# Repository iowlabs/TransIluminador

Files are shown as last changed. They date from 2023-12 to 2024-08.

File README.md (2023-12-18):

# TransIluminador

Un transiluminador es un instrumento utilizado en experimentos de biología molecular principalmente en procesos de electroforesis en aplicaciones de PCR, clonación, secuenciación o detección de ADN. Su principio se basa en transmitir luz de longitud e intensidad específica a travez de una muestra, lo cual permite visualizar proteinas específicas o ADN.

Para efectos de la instrumentación, consiste en un dispositivo que controla una gran cantidad de LEDs. De este modo, el dipositivo debe encargarse de generar los voltajes de operación y la corriente de los LEDs. Las variables objetivo para ser controladas son:

- voltaje de operación.
- Intensidad de iluminación.
- Tiempo de exposición.

En algunos dispositivos más complejos existen variables como tipos de curva de iluminación, o algunos cuentan con cámaras para la obtención de imagenes en el dispositivo mismo.
asdavsd

## Requisitos del dispositivo.

El dispositivo a desarrollar debe contar con las siguientes caracteristicas:

1. Alimentación de entrada de 12V. De esto se desprende que el dispositivo debe contar con un regulador DCDC tipo boost para los LEDs.

2. Capacidad de controlar diferentes configuraciónes de LEDs de salida.

3. Control de intensidad de los LEDs por medio de un control lineal de corriente.

4. Driver de corriente de hasta 1A por canal.

4. Capacidad para controlar de forma simultanea 2 canales.

5. Lazo de control para monitoreo y calibración de intensidad luminica.

6. Microcontrolador integrado.

7. Modo de operación manual, stand-alone con curvas pre-configuradas o modo de conexión a un host( pc o web app).

8. Monitoreo de la temperatura de los LEDs y sensor de temperatura externo.

9. Interfaz de usuario por medio de panel y pantalla OLED.

## Revisión del componentes.

Led driver de corriente ajustable

Modulo: LD06AJSA

Amazon: https://www.amazon.com/Adjustable-Current-Driver-30-1500mA-Constant/dp/B07S9C5QF1
Aliexpress: https://es.aliexpress.com/item/32848783838.html?gatewayAdapt=glo2esp

Datasheet no disponible, por observación es un potenciometro y una resistencia de 2.2k aparentemente
Parecido a ejemplos del datasheet de CN5711

Utiliza un CN5711

Datasheet: https://html.alldatasheet.com/html-pdf/1133252/CONSONANCE/CN5711/1403/2/CN5711.html

Otra opción pero más estrecho es NSI50150ADT4G controla entre 150 - 350 mA, 50V Vak max

Datasheet: https://www.onsemi.com/pdf/datasheet/nsi50150ad-d.pdf

Otra opción en rango similar al anterior es MAX16815 35mA - 100 mA
o MAX 16828 35mA - 200 mA
Voltaje de entrada entre 6.5 - 40 V

Datasheet: https://www.analog.com/media/en/technical-documentation/data-sheets/MAX16815-MAX16828.pdf

Existe la posibilidad de hacer una fuente de corriente con 2 PNP y 2 resistencias, la corriente resultante sera producto de ambas resistencias, se puede utilizar una entrada logica o directa para el funcionamiento, se puede reemplazar una ressitencia con un potenciometro y conseguir una fuente variable
Revisar archivo Modulo de corriente.asc

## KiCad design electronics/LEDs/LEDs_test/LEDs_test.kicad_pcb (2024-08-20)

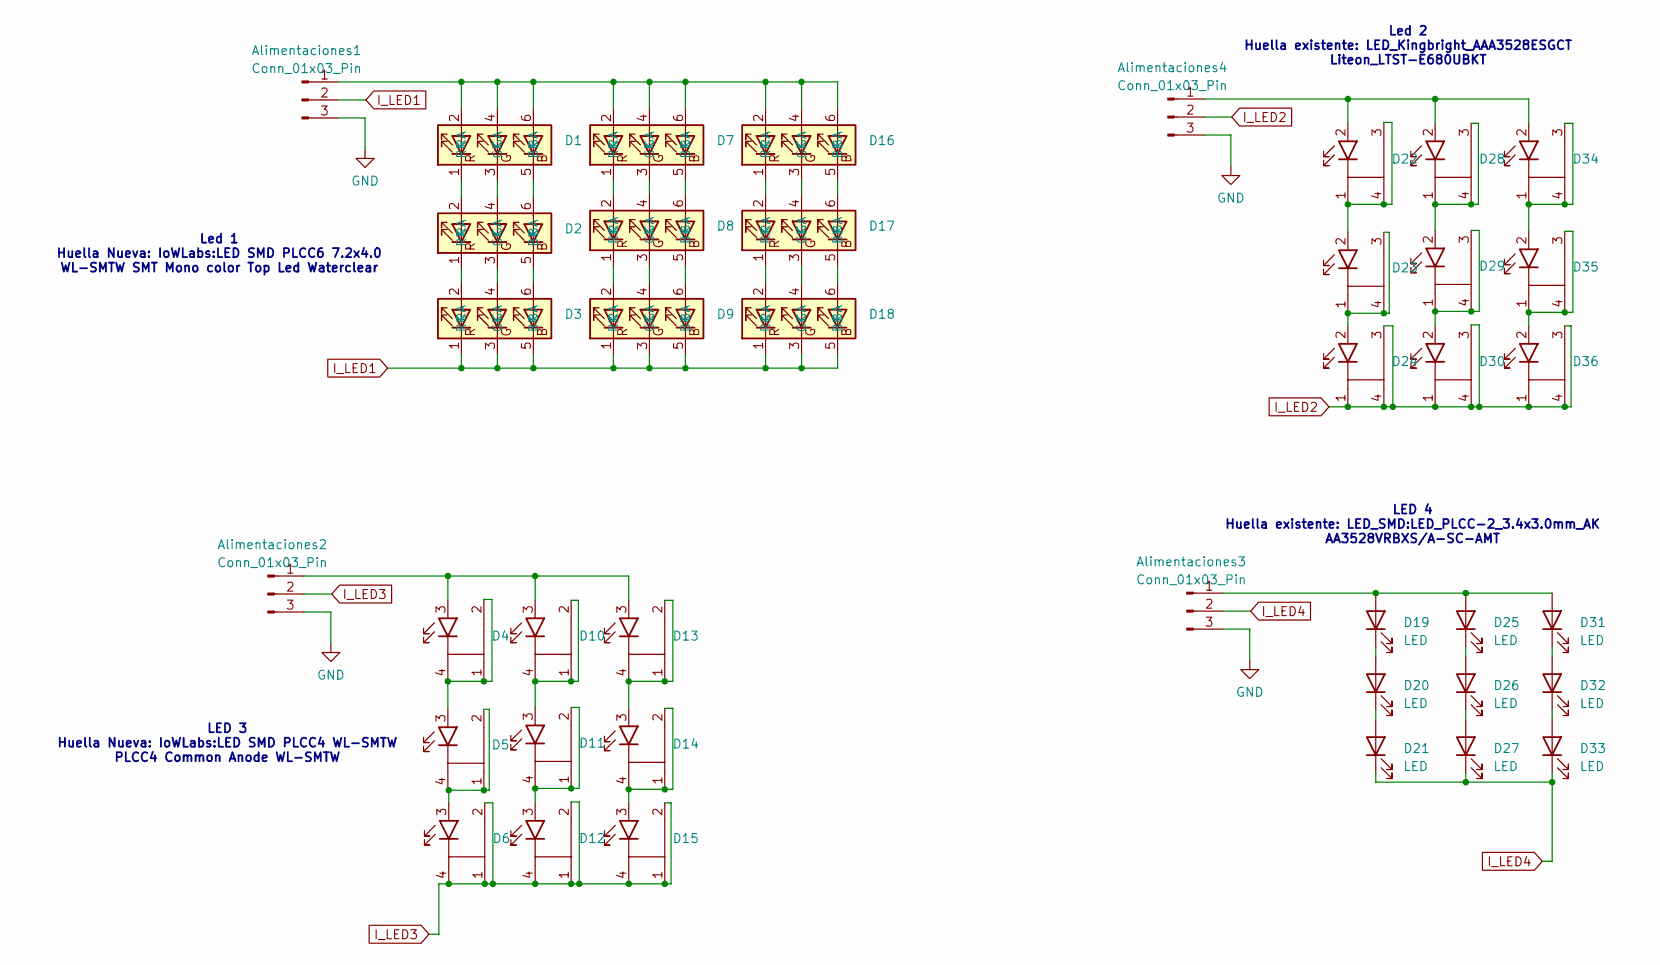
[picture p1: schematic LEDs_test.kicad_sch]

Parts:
Alimentaciones1, Alimentaciones2, Alimentaciones3, Alimentaciones4: Conn_01x03_Pin; JST_XH_B3B-XH-A_1x03_P2.50mm_Vertical
D1, D2, D3, D7, D8, D9, D16, D17, D18: LED SMD PLCC6 7.2x4.0
D4, D5, D6, D10, D11, D12, D13, D14, D15: LED SMD PLCC4 WL-SMTW
D19, D20, D21, D25, D26, D27, D31, D32, D33: LED; LED_PLCC-2_3.4x3.0mm_AK
D22, D23, D24, D28, D29, D30, D34, D35, D36: LED_Kingbright_AAA3528ESGCT

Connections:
GND: Alimentaciones1.3, Alimentaciones2.3, Alimentaciones3.3, Alimentaciones4.3
I_LED1: Alimentaciones1.2, D3.1 (RK), D3.3 (GK), D3.5 (BK), D9.1 (RK), D9.3 (GK), D9.5 (BK), D18.1 (RK), D18.3 (GK), D18.5 (BK)
I_LED2: Alimentaciones4.2, D24.1, D24.3, D24.4, D30.1, D30.3, D30.4, D36.1, D36.3, D36.4
I_LED3: Alimentaciones2.2, D6.1, D6.2, D6.4, D12.1, D12.2, D12.4, D15.1, D15.2, D15.4
I_LED4: Alimentaciones3.2, D21.1 (K), D27.1 (K), D33.1 (K)
unnamed: Alimentaciones1.1, D1.2 (RA), D1.4 (GA), D1.6 (BA), D7.2 (RA), D7.4 (GA), D7.6 (BA), D16.2 (RA), D16.4 (GA), D16.6 (BA)
unnamed: Alimentaciones2.1, D4.3, D10.3, D13.3
unnamed: Alimentaciones3.1, D19.2 (A), D25.2 (A), D31.2 (A)
unnamed: Alimentaciones4.1, D22.2, D28.2, D34.2
unnamed: D1.5 (BK), D2.6 (BA)
unnamed: D1.3 (GK), D2.4 (GA)
unnamed: D1.1 (RK), D2.2 (RA)
unnamed: D2.5 (BK), D3.6 (BA)
unnamed: D2.3 (GK), D3.4 (GA)
unnamed: D2.1 (RK), D3.2 (RA)
unnamed: D4.1, D4.2, D4.4, D5.3
unnamed: D5.1, D5.2, D5.4, D6.3
unnamed: D7.5 (BK), D8.6 (BA)
unnamed: D7.3 (GK), D8.4 (GA)
unnamed: D7.1 (RK), D8.2 (RA)
unnamed: D8.5 (BK), D9.6 (BA)
unnamed: D8.3 (GK), D9.4 (GA)
unnamed: D8.1 (RK), D9.2 (RA)
unnamed: D10.1, D10.2, D10.4, D11.3
unnamed: D11.1, D11.2, D11.4, D12.3
unnamed: D13.1, D13.2, D13.4, D14.3
unnamed: D14.1, D14.2, D14.4, D15.3
unnamed: D16.5 (BK), D17.6 (BA)
unnamed: D16.3 (GK), D17.4 (GA)
unnamed: D16.1 (RK), D17.2 (RA)
unnamed: D17.5 (BK), D18.6 (BA)
unnamed: D17.3 (GK), D18.4 (GA)
unnamed: D17.1 (RK), D18.2 (RA)
unnamed: D19.1 (K), D20.2 (A)
unnamed: D20.1 (K), D21.2 (A)
unnamed: D22.1, D22.3, D22.4, D23.2
unnamed: D23.1, D23.3, D23.4, D24.2
unnamed: D25.1 (K), D26.2 (A)
unnamed: D26.1 (K), D27.2 (A)
unnamed: D28.1, D28.3, D28.4, D29.2
unnamed: D29.1, D29.3, D29.4, D30.2
unnamed: D31.1 (K), D32.2 (A)
unnamed: D32.1 (K), D33.2 (A)
unnamed: D34.1, D34.3, D34.4, D35.2
unnamed: D35.1, D35.3, D35.4, D36.2

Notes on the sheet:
LED 4 Huella existente: LED_SMD:LED_PLCC-2_3.4x3.0mm_AK AA3528VRBXS/A-SC-AMT
Led 1 Huella Nueva: IoWLabs:LED SMD PLCC6 7.2x4.0 WL-SMTW SMT Mono color Top Led Waterclear
Led 2 Huella existente: LED_Kingbright_AAA3528ESGCT Liteon_LTST-E680UBKT
LED 3 Huella Nueva: IoWLabs:LED SMD PLCC4 WL-SMTW PLCC4 Common Anode WL-SMTW

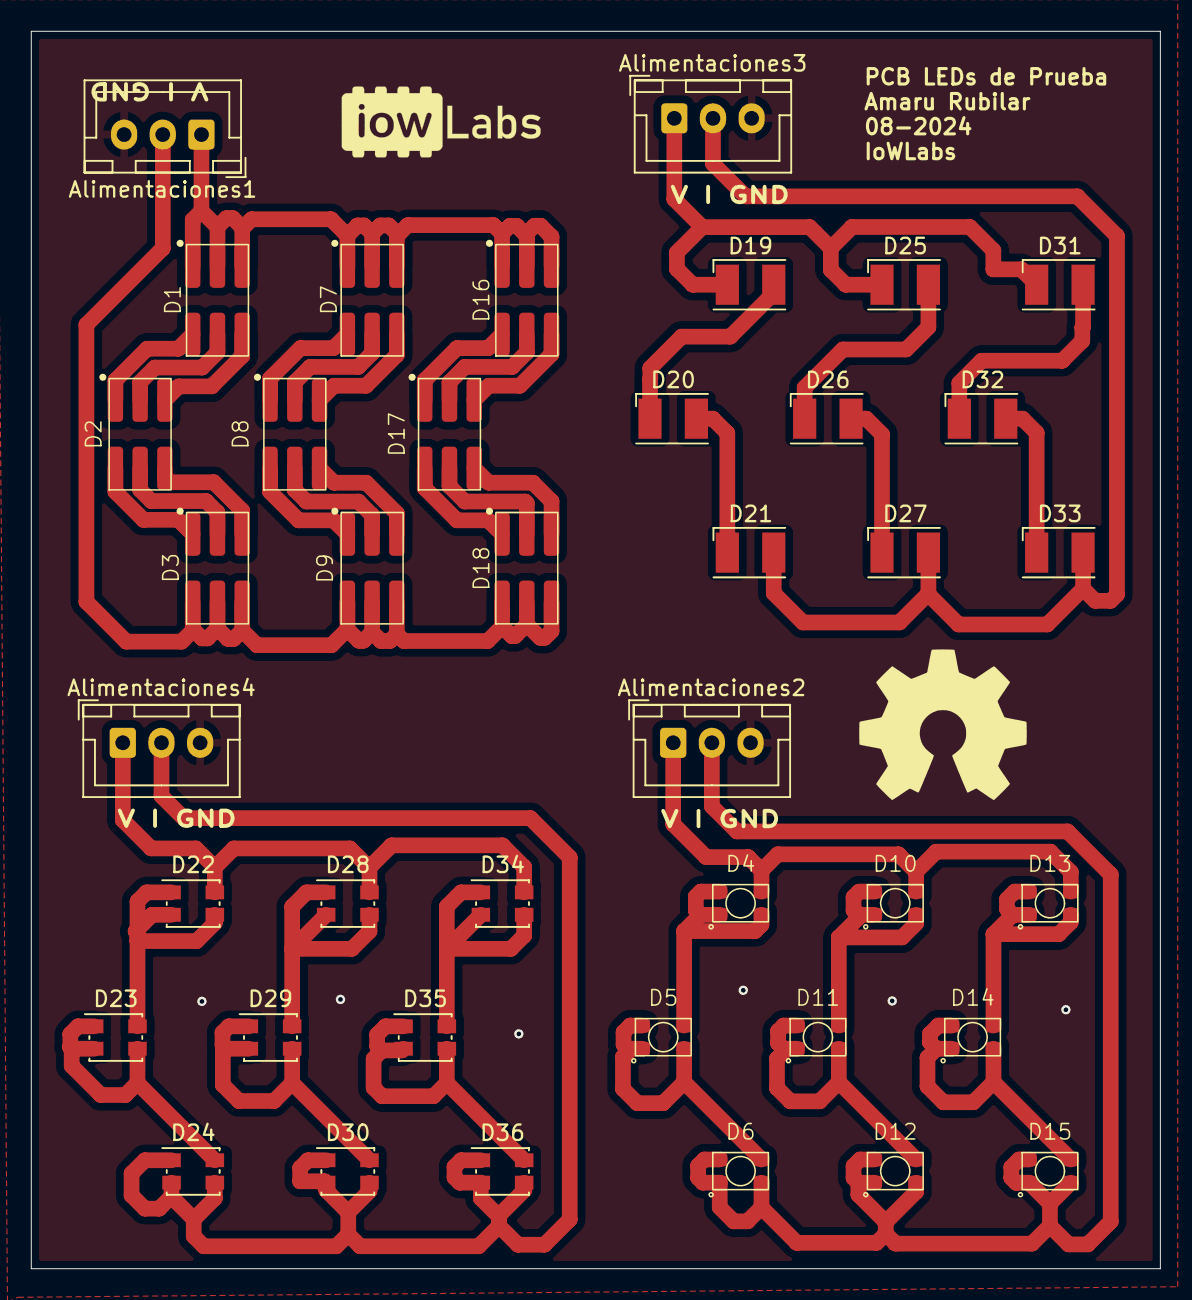
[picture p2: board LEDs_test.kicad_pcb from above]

Board: 2 copper layers, 73.0 x 80.0 mm, 40 parts (0 on the bottom side), 45 nets.

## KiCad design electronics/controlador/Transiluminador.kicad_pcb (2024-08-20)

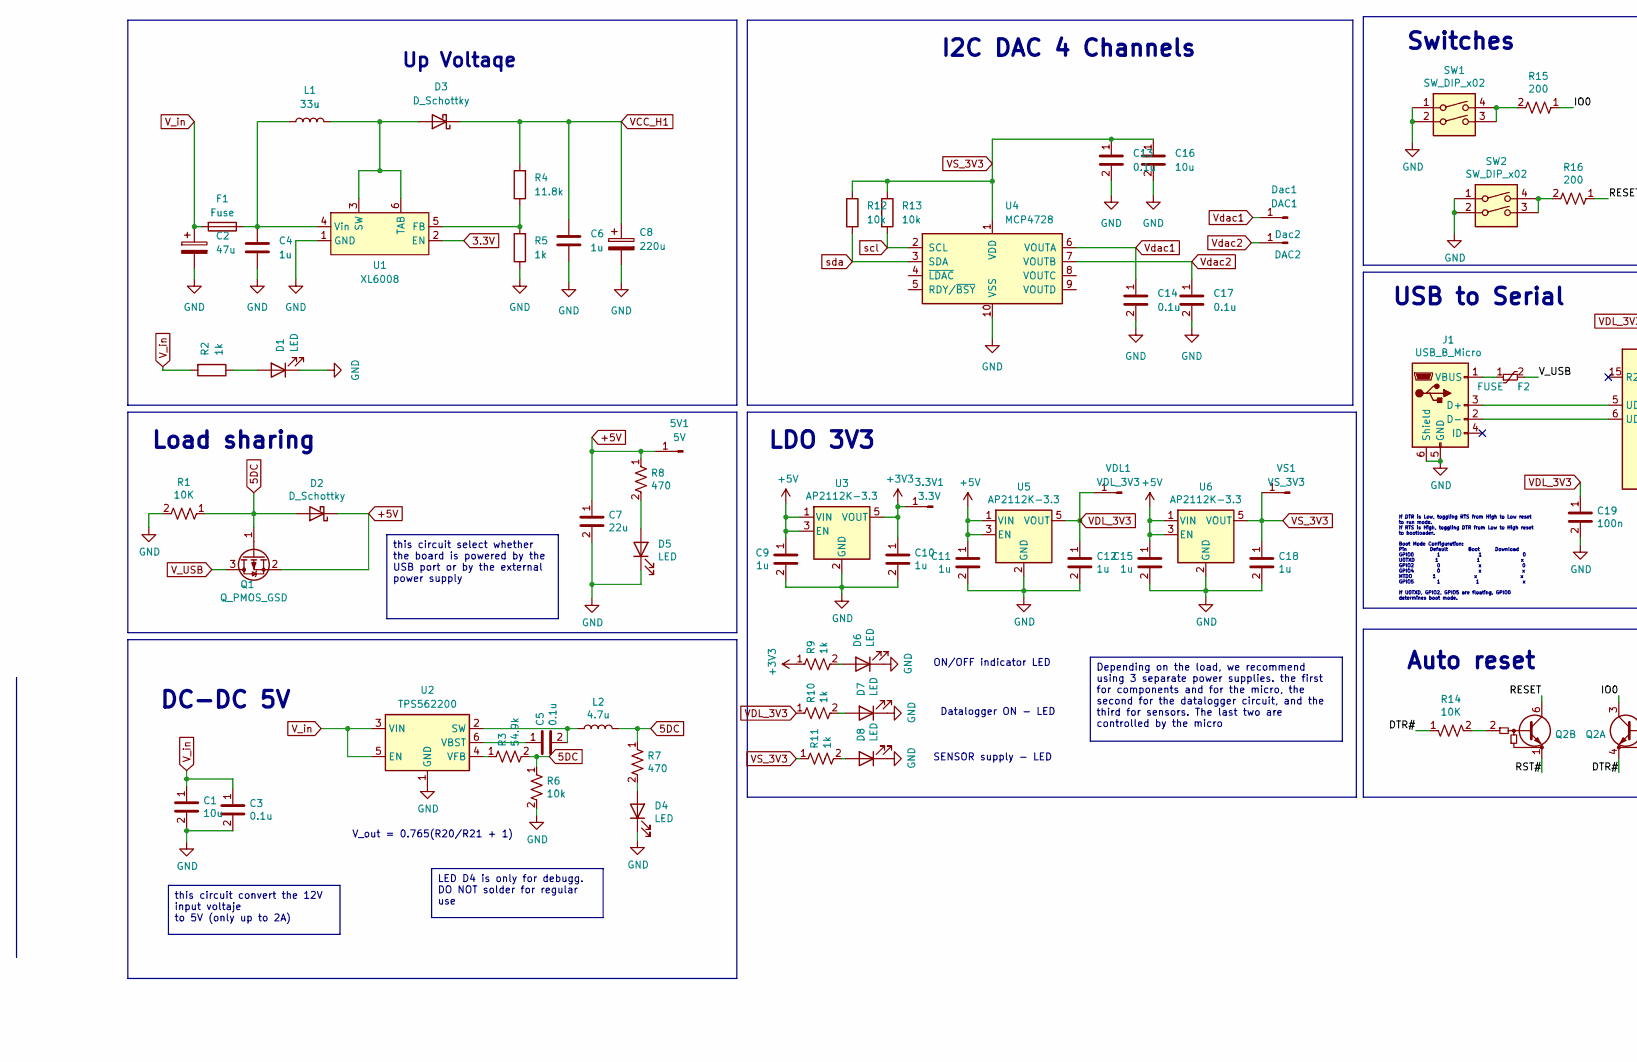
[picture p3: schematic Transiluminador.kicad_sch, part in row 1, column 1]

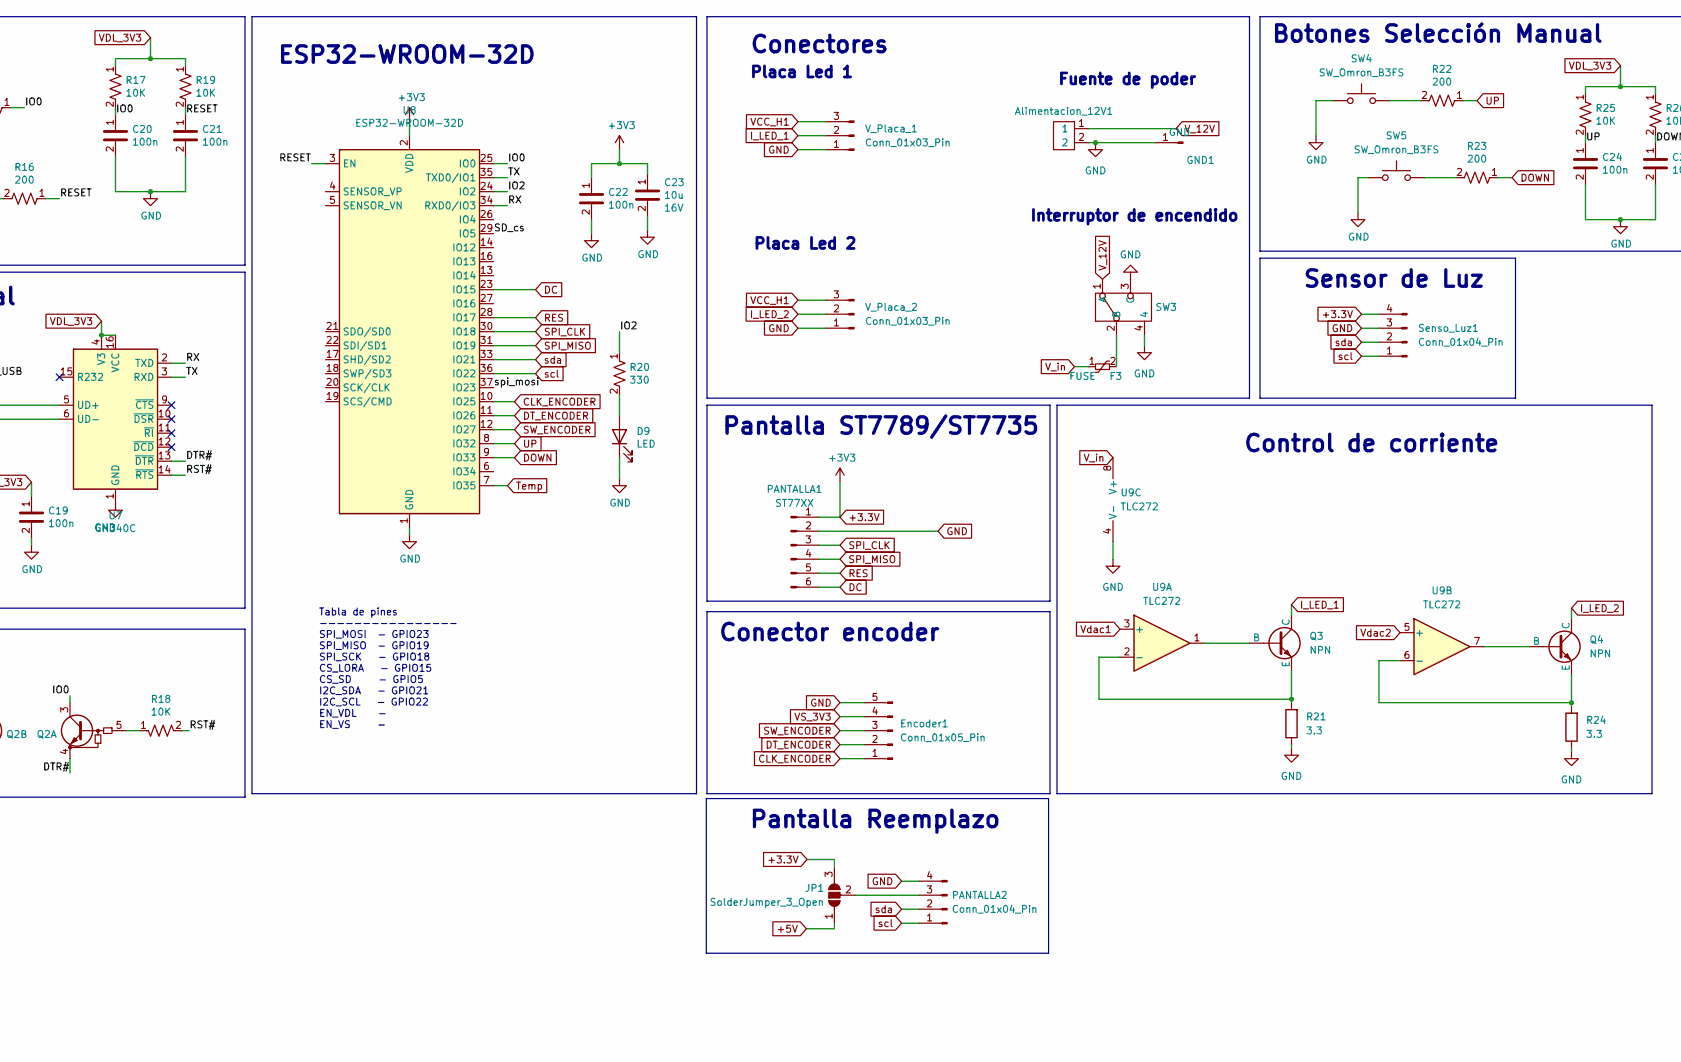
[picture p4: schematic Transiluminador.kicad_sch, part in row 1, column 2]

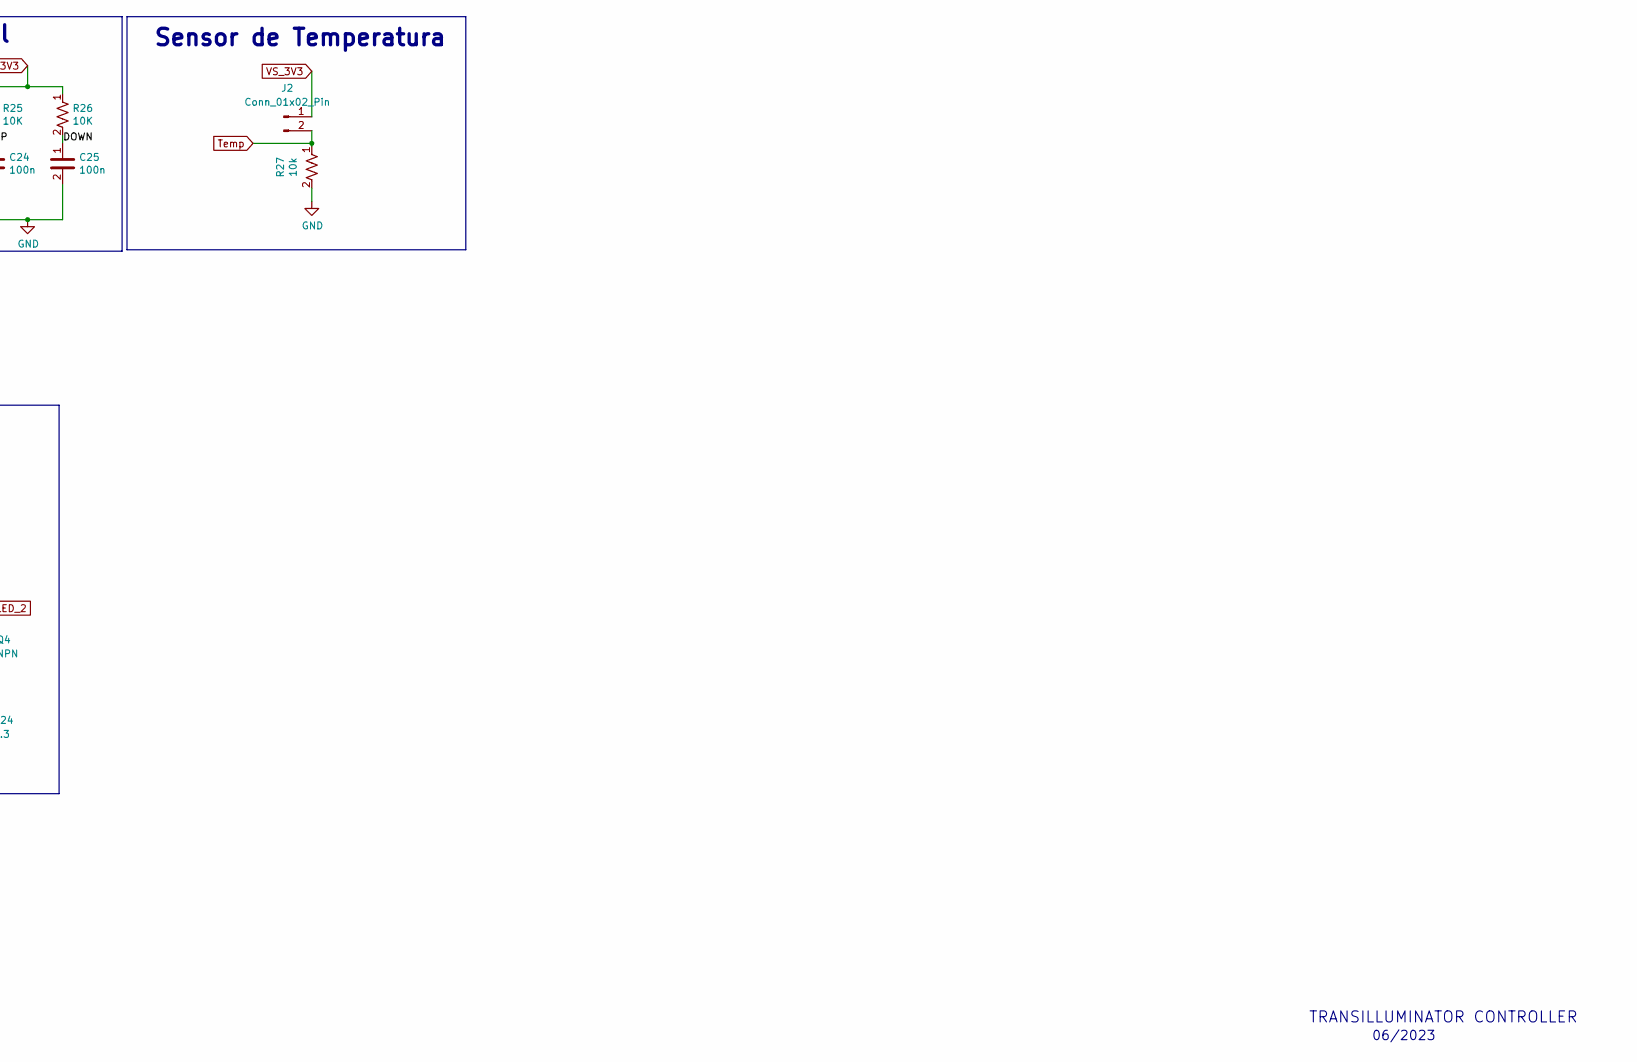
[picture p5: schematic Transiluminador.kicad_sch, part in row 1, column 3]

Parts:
3.3V1: 3.3V; TestPoint_Loop_D2.50mm_Drill1.0mm_LowProfile
5V1: 5V; TestPoint_Loop_D2.50mm_Drill1.0mm_LowProfile
Alimentacion_12V1: HDR-2x1; JST_XH_B2B-XH-A_1x02_P2.50mm_Vertical
C1, C23: 10u; C_0805_2012Metric; Voltage rated 16V
C2: 47u; CP_Elec_6.3x7.7
C3, C5: 0.1u; C_0805_2012Metric; Voltage rated 16V
C4, C6: 1u; C_0805_2012Metric
C7: 22u; C_0805_2012Metric; Voltage rated 16V
C8: 220u; CP_Elec_10x10.5
C9, C10, C11, C12, C15, C18: 1u; C_0603_1608Metric; Voltage rated 16V
C13, C14, C17: 0.1u; C_0603_1608Metric; Voltage rated 16V
C16: 10u; C_0603_1608Metric; Voltage rated 16V
C19, C20, C21, C22, C24, C25: 100n; C_0603_1608Metric; Voltage rated 16V
D1, D4, D5, D6, D7, D8, D9: LED; LED_0603_1608Metric
D2, D3: D_Schottky; D_SMA
Dac1: DAC1; TestPoint_Loop_D2.50mm_Drill1.0mm_LowProfile
Dac2: DAC2; TestPoint_Loop_D2.50mm_Drill1.0mm_LowProfile
Encoder1: Conn_01x05_Pin; JST_XH_B5B-XH-A_1x05_P2.50mm_Vertical
F1: Fuse; Fuse_1206_3216Metric
F2, F3: FUSE; Fuse_1206_3216Metric
GND1: GND; TestPoint_Loop_D2.50mm_Drill1.0mm_LowProfile
J1: USB_B_Micro; USB_Micro-B_Amphenol_10118194_Horizontal
J2: Conn_01x02_Pin; JST_XH_B2B-XH-A_1x02_P2.50mm_Vertical
JP1: SolderJumper_3_Open; SolderJumper-3_P1.3mm_Open_RoundedPad1.0x1.5mm
L1: 33u; L_12x12mm_H8mm
L2: 4.7u; L_Bourns_SRP7028A_7.3x6.6mm
PANTALLA1: ST77XX; JST_XH_B6B-XH-A_1x06_P2.50mm_Vertical
PANTALLA2: Conn_01x04_Pin; JST_XH_B4B-XH-A_1x04_P2.50mm_Vertical
Q1: Q_PMOS_GSD; SOT-23
Q2: Q_Dual_NPN_NPN_BRT_E1B1C2E2B2C1; SOT-363_SC-70-6_Handsoldering
Q3, Q4: NPN; SOT-223-3_TabPin2
R1, R14, R17, R18, R19, R25, R26: 10K; R_0603_1608Metric
R2, R5, R9, R10, R11: 1k; R_0603_1608Metric
R3: 54.9k; R_0603_1608Metric
R4: 11.8k; R_0603_1608Metric
R6, R12, R13, R27: 10k; R_0603_1608Metric
R7, R8: 470; R_0603_1608Metric
R15, R16, R22, R23: 200; R_0603_1608Metric
R20: 330; R_0603_1608Metric
R21, R24: 3.3; TO-263-3 TAB 3
SW1, SW2: SW_DIP_x02; SMD_SWITCH
SW3: SS-SK12D07VG4-SDDT
SW4, SW5: SW_Omron_B3FS; JST_XH_B2B-XH-A_1x02_P2.50mm_Vertical
Senso_Luz1: Conn_01x04_Pin; JST_XH_B4B-XH-A_1x04_P2.50mm_Vertical
U1: XL6008; TO-252-5_TabPin6
U2: TPS562200; SOT-23-6
U3, U5, U6: AP2112K-3.3; SOT-23-5
U4: MCP4728; MSOP-10_3x3mm_P0.5mm
U7: CH340C; SOIC-16_3.9x9.9mm_P1.27mm
U8: ESP32-WROOM-32D; ESP32-WROOM-32
U9: TLC272; SOIC-8_3.9x4.9mm_P1.27mm
VDL1: VDL_3V3; TestPoint_Loop_D2.50mm_Drill1.0mm_LowProfile
VS1: VS_3V3; TestPoint_Loop_D2.50mm_Drill1.0mm_LowProfile
V_Placa_1, V_Placa_2: Conn_01x03_Pin; JST_XH_B3B-XH-A_1x03_P2.50mm_Vertical

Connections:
3.3V: U1.2 (EN)
5DC: D2.2 (A), L2.2, Q1.1 (G), R1.1, R3.2, R6.1, R7.1
+3.3V: 3.3V1.1, C10.1, C22.1, C23.1, JP1.3 (B), PANTALLA1.1, R9.1, Senso_Luz1.4, U3.5 (VOUT), U8.2 (VDD)
+5V: 5V1.1, C7.1, C9.1, C11.1, C15.1, D2.1 (K), JP1.1 (A), Q1.2 (S), R8.1, U3.1 (VIN), U3.3 (EN), U5.1 (VIN), U5.3 (EN), U6.1 (VIN), U6.3 (EN)
/DTR#: Q2.4 (E1), R14.1, U7.13 (~DTR)
/IO0: C20.1, Q2.3 (C1), R15.1, R17.2, U8.25 (IO0)
/IO2: R20.1, U8.24 (IO2)
/RESET: C21.1, Q2.6 (C1), R16.1, R19.2, U8.3 (EN)
/RST#: Q2.1 (E1), R18.2, U7.14 (~RTS)
/RX: U7.2 (TXD), U8.34 (RXD0/IO3)
/SD_cs: U8.29 (IO5)
/TX: U7.3 (RXD), U8.35 (TXD0/IO1)
/spi_mosi: U8.37 (IO23)
CLK_ENCODER: Encoder1.1, U8.10 (IO25)
DC: PANTALLA1.6, U8.23 (IO15)
DOWN: C25.1, R23.1, R26.2, U8.9 (IO33)
DT_ENCODER: Encoder1.2, U8.11 (IO26)
GND: Alimentacion_12V1.2, C1.2, C2.2, C3.2, C4.2, C6.2, C7.2, C8.2, C9.2, C10.2, C11.2, C12.2, C13.2, C14.2, C15.2, C16.2, C17.2, C18.2, C19.2, C20.2, C21.2, C22.2, C23.2, C24.2, C25.2, D1.1 (K), D4.1 (K), D5.1 (K), D6.1 (K), D7.1 (K), D8.1 (K), D9.1 (K), Encoder1.5, GND1.1, J1.5 (GND), J1.6 (Shield), PANTALLA1.2, PANTALLA2.4, R1.2, R5.1, R6.2, R21.1, R24.1, R27.2, SW1.1, SW1.2, SW2.1, SW2.2, SW3.3 (C), SW3.4, SW4.1, SW5.1, Senso_Luz1.3, U1.1 (GND), U2.1 (GND), U3.2 (GND), U4.10 (VSS), U5.2 (GND), U6.2 (GND), U7.1 (GND), U8.1 (GND), U8.15 (GND), U8.38 (GND), U8.39 (GND), U9.4 (V-), V_Placa_1.1, V_Placa_2.1
I_LED_1: Q3.1 (C), V_Placa_1.2
I_LED_2: Q4.1 (C), V_Placa_2.2
unnamed: D1.2 (A), R2.1
unnamed: D3.2 (A), L1.2, U1.3 (SW), U1.6 (TAB)
unnamed: D4.2 (A), R7.2
unnamed: D5.2 (A), R8.2
unnamed: D6.2 (A), R9.2
unnamed: D7.2 (A), R10.2
unnamed: D8.2 (A), R11.2
unnamed: D9.2 (A), R20.2
unnamed: J1.3 (D+), U7.5 (UD+)
unnamed: J1.2 (D-), U7.6 (UD-)
unnamed: F2.1, J1.1 (VBUS)
unnamed: JP1.2 (C), PANTALLA2.3
unnamed: Q2.5 (B1), R18.1
unnamed: Q2.2 (B1), R14.2
unnamed: Q3.2 (B), U9.1
unnamed: Q3.3 (E), R21.2, U9.2 (-)
unnamed: Q4.2 (B), U9.7
unnamed: Q4.3 (E), R24.2, U9.6 (-)
unnamed: R15.2, SW1.3, SW1.4
unnamed: R16.2, SW2.3, SW2.4
unnamed: R22.2, SW4.2
unnamed: R23.2, SW5.2
unnamed: F3.2, SW3.2 (B)
unnamed: R4.1, R5.2, U1.5 (FB)
unnamed: C4.1, F1.1, L1.1, U1.4 (Vin)
unnamed: C5.2, L2.1, U2.2 (SW)
unnamed: C5.1, U2.6 (VBST)
unnamed: R3.1, U2.4 (VFB)
RES: PANTALLA1.5, U8.28 (IO17)
SPI_CLK: PANTALLA1.3, U8.30 (IO18)
SPI_MISO: PANTALLA1.4, U8.31 (IO19)
SW_ENCODER: Encoder1.3, U8.12 (IO27)
Temp: J2.2, R27.1, U8.7 (IO35)
UP: C24.1, R22.1, R25.2, U8.8 (IO32)
VCC_H1: C6.1, C8.1, D3.1 (K), R4.2, V_Placa_1.3, V_Placa_2.3
VDL_3V3: C12.1, C19.1, R10.1, R17.1, R19.1, R25.1, R26.1, U5.5 (VOUT), U7.4 (V3), U7.16 (VCC), VDL1.1
VS_3V3: C13.1, C16.1, C18.1, Encoder1.4, J2.1, R11.1, R12.1, R13.1, U4.1 (VDD), U6.5 (VOUT), VS1.1
V_12V: Alimentacion_12V1.1, SW3.1 (A)
V_USB: F2.2, Q1.3 (D)
V_in: C1.1, C2.1, C3.1, F1.2, F3.1, R2.2, U2.3 (VIN), U2.5 (EN), U9.8 (V+)
Vdac1: C14.1, Dac1.1, U4.6 (VOUTA), U9.3 (+)
Vdac2: C17.1, Dac2.1, U4.7 (VOUTB), U9.5 (+)
scl: PANTALLA2.1, R13.2, Senso_Luz1.1, U4.2 (SCL), U8.36 (IO22)
sda: PANTALLA2.2, R12.2, Senso_Luz1.2, U4.3 (SDA), U8.33 (IO21)

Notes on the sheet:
LED D4 is only for debugg. DO NOT solder for regular use
Depending on the load, we recommend using 3 separate power supplies. the first for components and for the micro, the second for the datalogger circuit, and the third for sensors. The last two are controlled by the micro
this circuit select whether the board is powered by the USB port or by the external power supply
this circuit convert the 12V input voltaje to 5V (only up to 2A)
USB to Serial
Pantalla Reemplazo
I2C DAC 4 Channels
Placa Led 1
Placa Led 2
Tabla de pines ---------------- SPI_MOSI - GPIO23 SPI_MISO - GPIO19 SPI_SCK - GPIO18 CS_LORA - GPIO15 CS_SD - GPIO5 I2C_SDA - GPIO21 I2C_SCL - GPIO22 EN_VDL - EN_VS -
SENSOR supply - LED
Pantalla ST7789/ST7735
Conectores
Interruptor de encendido
Fuente de poder
06/2023
Up Voltaqe
DC-DC 5V
Switches
Auto reset
ESP32-WROOM-32D
If DTR is Low, toggling RTS from High to Low reset to run mode. If RTS is High, toggling DTR from Low to High reset to bootloader. Boot Mode Configuration: Pin Default Boot Download GPIO0 1 1 0 U0TXD 1 1 x GPIO2 0 x 0 GPIO4 0 x x MTDO 1 x x GPIO5 1 1 x If U0TXD, GPIO2, GPIO5 are floating, GPIO0 det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
V_out = 0.765(R20/R21 + 1)
ON/OFF indicator LED
Control de corriente
LDO 3V3
Botones Selección Manual
Load sharing
Conector encoder
Sensor de Luz
TRANSILLUMINATOR CONTROLLER
Sensor de Temperatura
Datalogger ON - LED

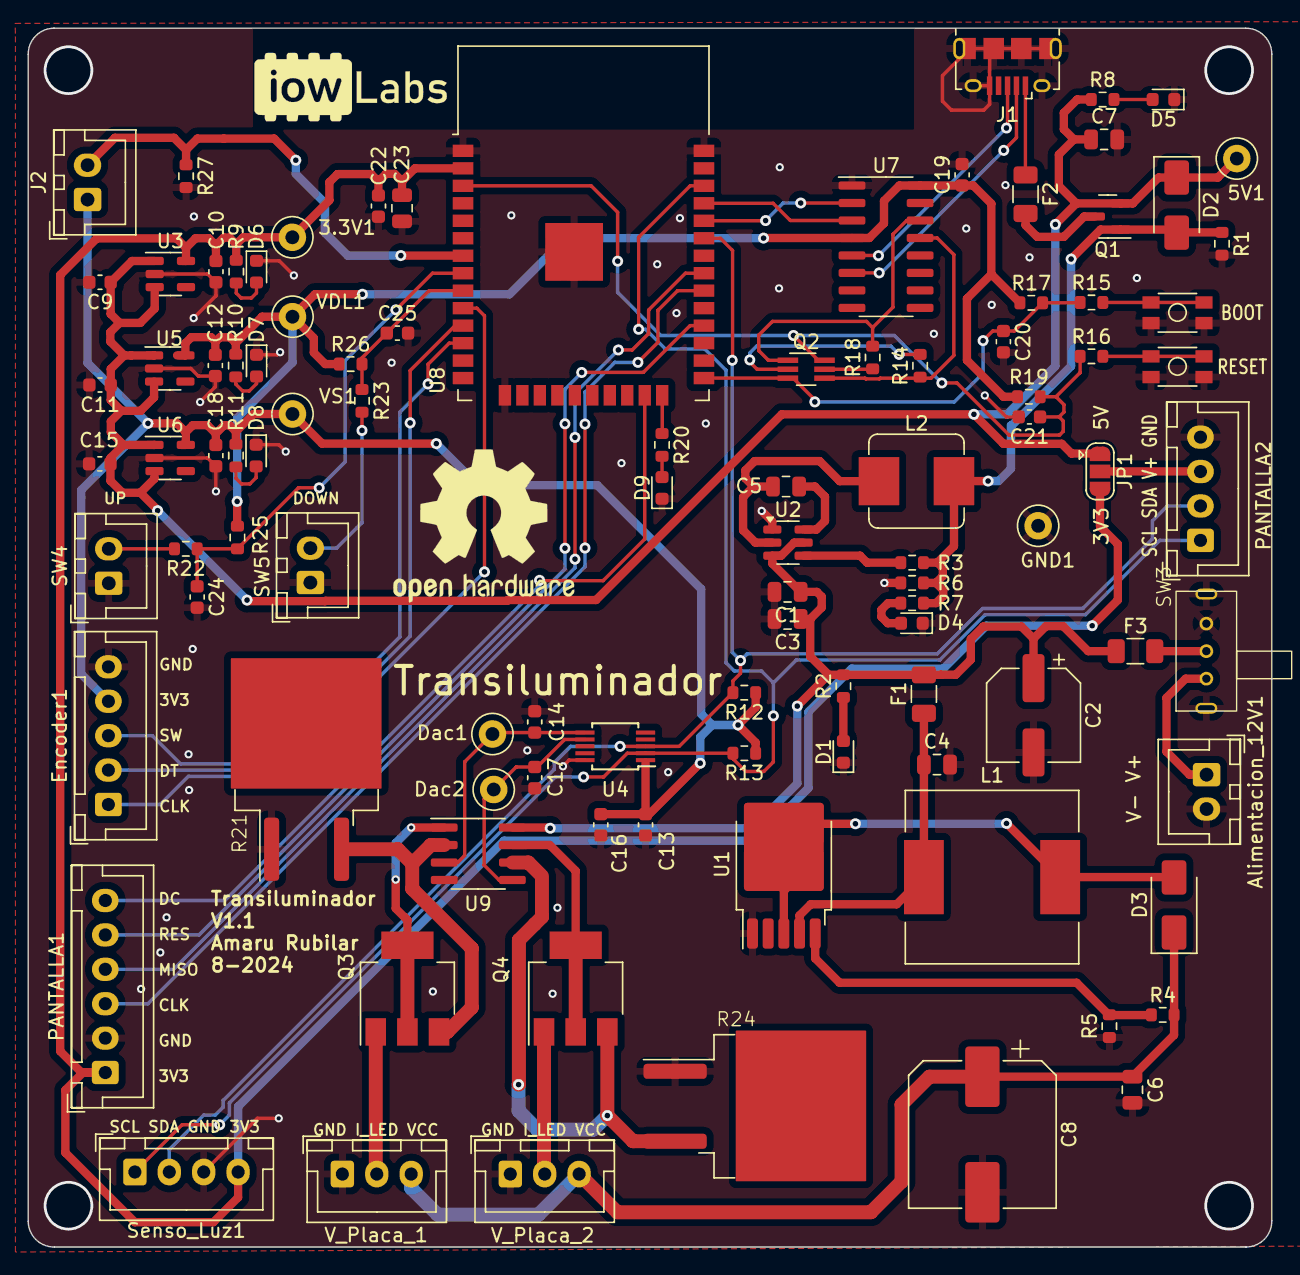
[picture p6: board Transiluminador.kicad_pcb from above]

Board: 2 copper layers, 90.3 x 88.5 mm, 101 parts (0 on the bottom side), 61 nets.

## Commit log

2023-12-15 adding requirements
    [LEDs_10x10.kicad_pcb, LEDs_10x10.kicad_sch, Transiluminador.kicad_pcb, Transiluminador.kicad_sch]
2023-12-18 adding blue LEDS datasheet
2023-12-18 actualización
    [Transiluminador.kicad_sch]
2024-08-19 changing name for folder hardware
    [LEDs_10x10.kicad_pcb, LEDs_10x10.kicad_sch, Transiluminador-B_Cu.gbl, Transiluminador-B_Mask.gbs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]
